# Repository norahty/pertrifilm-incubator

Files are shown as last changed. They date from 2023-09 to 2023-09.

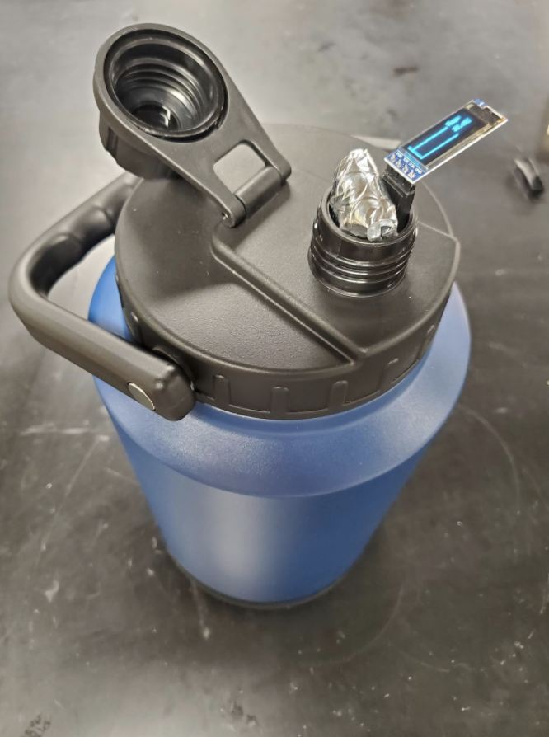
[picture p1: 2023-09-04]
Tests/Ease of Use Test/Final Solution.png

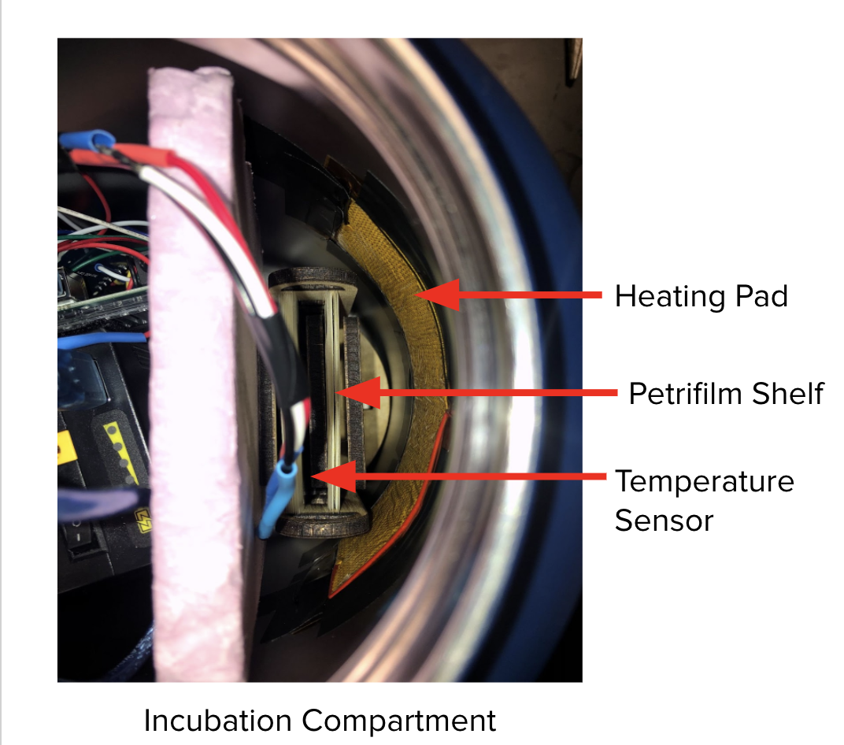
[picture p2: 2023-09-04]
Tests/Ease of Use Test/Incubation Chamber.png

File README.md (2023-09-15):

# Pertrifilm-Incubator Coding Project

This Arduino-based project is coded using C++ to build a portable Petrifilm incubator (a system to inspect e.coli water contamination) for water sample testing in underprivileged areas. It is designed for temperature control in an incubator. It uses various hardware components and libraries to maintain a stable temperature environment for specific applications. This pertrifilm incubator is currently being applied to use by onsite researchers. Below, you will find information on the hardware required, connections, warnings, and the libraries needed for this project.

## Hardware

You will need the following hardware components for this project:

1. 1 x DS18B20 Temperature Sensor
2. 1 x 12V Heater
3. 1 x MOSFET Module (MOS)
4. 1 x Buzzer
5. 1 x Arduino Mega 2560
6. 1 x 0.92 inch OLED Display
7. 1 x SD Card Module
8. Battery (Power Supply)

## Connections

Follow these steps to connect the hardware components to the Arduino Mega 2560:

1. Connect all 5V pins of the components to the Arduino's 5V pin.
2. Connect all GND (Ground) pins of the components to the Arduino's GND.
3. Connect the MOSFET module's IN pin to Arduino's D4.
4. Connect the buzzer to Arduino's D3.
5. Connect the middle pin of the DS18B20 temperature sensor to Arduino's D5.
6. Connect the OLED display's SCL pin to Arduino's SCL.
7. Connect the OLED display's SDA pin to Arduino's SDA.
8. Connect the SD card module's MISO pin to Arduino's 50.
9. Connect the SD card module's MOSI pin to Arduino's 51.
10. Connect the SD card module's SCK pin to Arduino's 52.
11. Connect the SD card module's CS pin to Arduino's 53.

## Warnings

Please take note of the following warnings:

1. Do not set the timer to be lower than or equal to 500ms.
2. Do not touch the heating pad while it is working.
3. Do not let the sensor touch the heater directly.

## Required Libraries

Make sure to install the following libraries in your Arduino IDE before uploading the code:

1. `Adafruit_SSD1306`: Library for OLED display.
2. `DallasTemperature`: Library for DS18B20 temperature sensor.
3. `MsTimer2`: Library for managing timers.

## Arduino Code

You can find the Arduino code for this project in the provided code file. Simply upload this code to your Arduino Mega 2560 to start using the incubator temperature control system.

## Usage

This incubator temperature control system continuously monitors the temperature using the DS18B20 sensor and displays it on the OLED display. It also controls the heater and buzzer based on predefined temperature thresholds. Temperature data is saved to an SD card for later analysis.

Feel free to modify the code and customize the temperature control settings to suit your specific incubation needs.

Enjoy your Arduino-based incubator temperature control project!


Here's a simple demo of how the system works:

temperature control demo:

https://github.com/norahty/pertrifilm-incubator/assets/94091909/2bb5951b-de06-4672-81f7-e4776b39d3b2

the entire incubator:

https://github.com/norahty/pertrifilm-incubator/assets/94091909/0f1d060a-ad9f-48bf-81df-5f7a59860c57

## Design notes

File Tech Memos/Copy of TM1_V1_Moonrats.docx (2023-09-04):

DATE: February 8th, 2021

TO: Dr. Deirdre Hunter

FROM: Sindhuja Darisipudi, Nora Han, Joseph Urso, Michael Tang, Jason Ye

Team Moonrats (5moonrats@gmail.com)

SUBJECT: Water Assessment Incubator Problem Statement and Team Structure

Design Problem Context

Water sanitation is a crisis affecting 780 million people around the world, many of whom live in underprivileged and remote areas. This problem is exacerbated because not all water potability tests (i.e. tests that indicate if water is drinkable) are practical in such settings, as many rely on access to laboratories. One method that does work is via Petrifilms, a culture-based method for detection.

Culture-based methods for the detection of microbial contaminants are the state-of-the-art for water quality analysis in both industrialized and developing countries. Microorganisms exist in many environments and require different temperature conditions for optimal growth. Therefore, creating a temperature-stable incubation environment is a precondition for the reliable detection of microbial contaminants of concern in drinking water. By applying water samples to these Petrifilms and incubating them for 24-48 hours, one can visually inspect for E. coli contamination.

Hence, our task is to build an incubator for the Petrifilms that is suitable for water sanitation tests in these remote areas. Our main design criteria in accomplishing this, as discussed with our client, include small size, ease of use, and data logging capabilities, as elaborated in our problem statement.

Current Design Flaws and Future Solutions:

1. Design solution:

A portable, low-cost incubator for holding petri films will be designed by our team.

Designed for: Public Invention, as a part of an initiative to help monitor water quality in remote settings.

Used by: On the ground experts in remote and low resource settings

2. Limitations of existing solution

In order to monitor water quality in remote & low resource settings, a portable incubator is needed to be transportable, as on the ground workers will often be going from location to location

The existing solution has the limitations of:

i. not providing enough information about the inside temperature to monitor the growing environment of the microorganisms.

ii. not being small enough

3. Potential design solution features

A portable (< 38cm×24.5cm×19cm (dimensions of existing design))*, low-cost (under $500) incubator to hold 20 small petri film (3x4 inches) which has:

i. the ability to provide a constant elevated temperature between 30ºC and 42ºC, as this is the ideal incubation temperature for the petrifilms

ii. a data tracking and digital readout of temperature

iii. rechargeable primary cells that could last the duration of one incubation cycle (up to 48 hours) per one charging

iv. be able to work with minimal repairs for upwards of 3 years

If possible, we would like to have it the following features:

i. A warning mechanism to indicate if the system has failed, the battery is low, or if the temperature has fluctuated out of range.

iii. humidity control inside of the incubator

*client wants it to fit in a backpack.

Team Structures and Activities

Over the course of the Spring 2021 semester (beginning January 25th, 2021 and ending May 14th, 2021), Team Moonrats will produce a prototype, 9 technical memos, and a final design accompanying the final prototype. Table 1 outlines the authors of each technical memo, and the date by which we plan to finish them. Table 2 outlines other major deliverables and an estimate of when we would like to finish them by.

We will produce our deliverables within a $500 budget that has been allocated to our team. In order to meet our goals within the given time frame, we will meet weekly on Tuesdays from 7:00pm - 8:00pm. Below, Table 3 and Table 4 list the contact information of the members and affiliates of Team Moonrats.

Table 1: Tech Memo Author Table

Tech Memo | Finish By | Authors
TM1: Problem Statement | 02/08/2021 | All team members
TM 2: Need-to-Know List and Bibliography | 02/15/2021 | Michael & Joseph
TM 3: Design Criteria | 02/19/2021 | Jason & Nora
TM 4: Brainstorming of design solutions | 02/22/2021 | Sindhuja & Michael
SM 10: Team Pit Stop Reflection | 02/22/2021 | Everyone individually
TM 5: Evaluation of Design Solution | 03/02/2021 | Joseph & Jason
TM 6: Design Plan | 03/08/2021 | Nora & Sindhuja
TM 7: Gantt Chart | 03/22/2021 | Michael & Joseph
SM 11: Identity Reflection | 03/29/2021 | Everyone individually
TM 8: Testing Plan | 04/12/2021 | Jason & Nora
TM 9: Design Solution | 05/05/2021 | All team members
SM 12: Team Post Mortem Reflection | 05/07/2021 | Everyone individually

Table 2: Major Deliverables and Planned Completion Dates

Task | Planned Completion Date
Initial Low Fidelity Prototypes | 1st Week of March
Final Low Fidelity Prototype | 2nd Week of March
Select Design & Order Materials | 3rd Week of March
Final Design & Prototype | Late April

Table 3: Team Members and Contact Information

Team Moonrats
Name | Email | Phone Number
Joseph Urso | jru1@rice.edu | +1 (832) 496-4116
Jason Ye | jy76@rice.edu | +1 (832) 245-6714
Sindhuja Darisipudi | sd87@rice.edu | +1 (972) 662-8299
Michael Tang | mjt6@rice.edu | +1 (713) 349-3952
Nora Han | th42@rice.edu | +86 131 4118 1917

Table 4: Clients, Sponsors, and Other Affiliates and Contact Information

Name | Role | Email
Dr. Christopher Ferguson | Client | cfergu11@gmail.com
Dr. Ashley Taylor | Faculty Sponsor | art6@rice.edu
Scott Lin | Design Mentor | sl105@rice.edu
Cat Grasso | Writing Mentor | cg39@rice.edu

Works Cited

“Global WASH Fast Facts.” Global Water, Sanitation, & Hygiene (WASH), Center for Disease Control and Prevention, 11 April 2016, https://www.cdc.gov/healthywater/global/wash_statistics.html. Accessed 5 February 2021.

Mistry, Pratibha, and Jessica A. Lawson. “Testing water quality: When labs don’t work.” World Bank Blogs, World Bank Group, 24 January 2017, https://blogs.worldbank.org/water/when-labs-don-t-work. Accessed 7 February 2021.

Schertenleib, A., Sigrist, J., Friedrich, M. N. D., Ebi, C., Hammes, F., Marks, S. J. Construction of a Low-cost Mobile Incubator for Field and Laboratory Use. J. Vis. Exp. (145), e58443, doi:10.3791/58443 (2019). Accessed 7 February 2021.

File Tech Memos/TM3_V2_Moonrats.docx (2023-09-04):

DATE: March 2nd, 2021

TO: Dr. Deirdre Hunter

FROM: Sindhuja Darisipudi, Nora Han, Joseph Urso, Michael Tang, Jason Ye[^1]

Team Moonrats (5moonrats@gmail.com)

SUBJECT: Water Assessment Incubator Design Criteria

Introduction

1. Relevant Context for the Engineering Design Process

Our client needs a 3M™ E. coli detection Petrifilm[^2] incubator to provide a stable temperature environment for 24-48 hours. Currently, he has identified several problems with their existing incubator (“The Armadillo Incubator”) and has asked us to create an improved, low-cost and portable incubator for these Petrifilms that is suitable for water sanitation testing research in remote areas that lack lab resources.

According to our previous meeting with our client, we identified several potential design solution features of a portable, low-cost incubator to hold 20 small petri film (3x4 inches) which has: the ability to provide a constant elevated temperature; a data tracking and digital readout of temperature; rechargeable primary cells that could last the duration of one incubation cycle per one charging; be able to work with minimal repairs. If possible, we would like to have the following features: a warning mechanism to indicate if the system has failed, the battery is low, or if the temperature has fluctuated out of range; a humidity control inside of the incubator

2. Overview of Decision Process & Reasons of Research decisions

Our team generated a list of design criteria and constraints during class discussion (Feb, 9, 2021) and our weekly team meeting (Feb, 9, 2021). The constraints of our design criteria are mainly based on client requests and quantitative research. In some cases, the client has provided us with quantitative requirements, whose parameters agree with our additional research. The objectives are mainly based on client requests and will be evaluated by the users. Detailed explanations of each criteria are included in the conclusion section. We started by listing out the criteria without the numbers (low cost, small size, easy to make, easy to use, be in temperature range, battery life, durability, battery alarm, temperature alarm, data tracking system). Then, on the basis of our interview with our client (Feb, 5, 2021), we identified which criterias are constraints (be in temperature range, and safety) based on our need-to-know list and research in TM_2. Finally, we confirmed a reasonable list of design criteria (low cost, size, easy to make, easy to use, durability, battery duration and adjustable temperature).

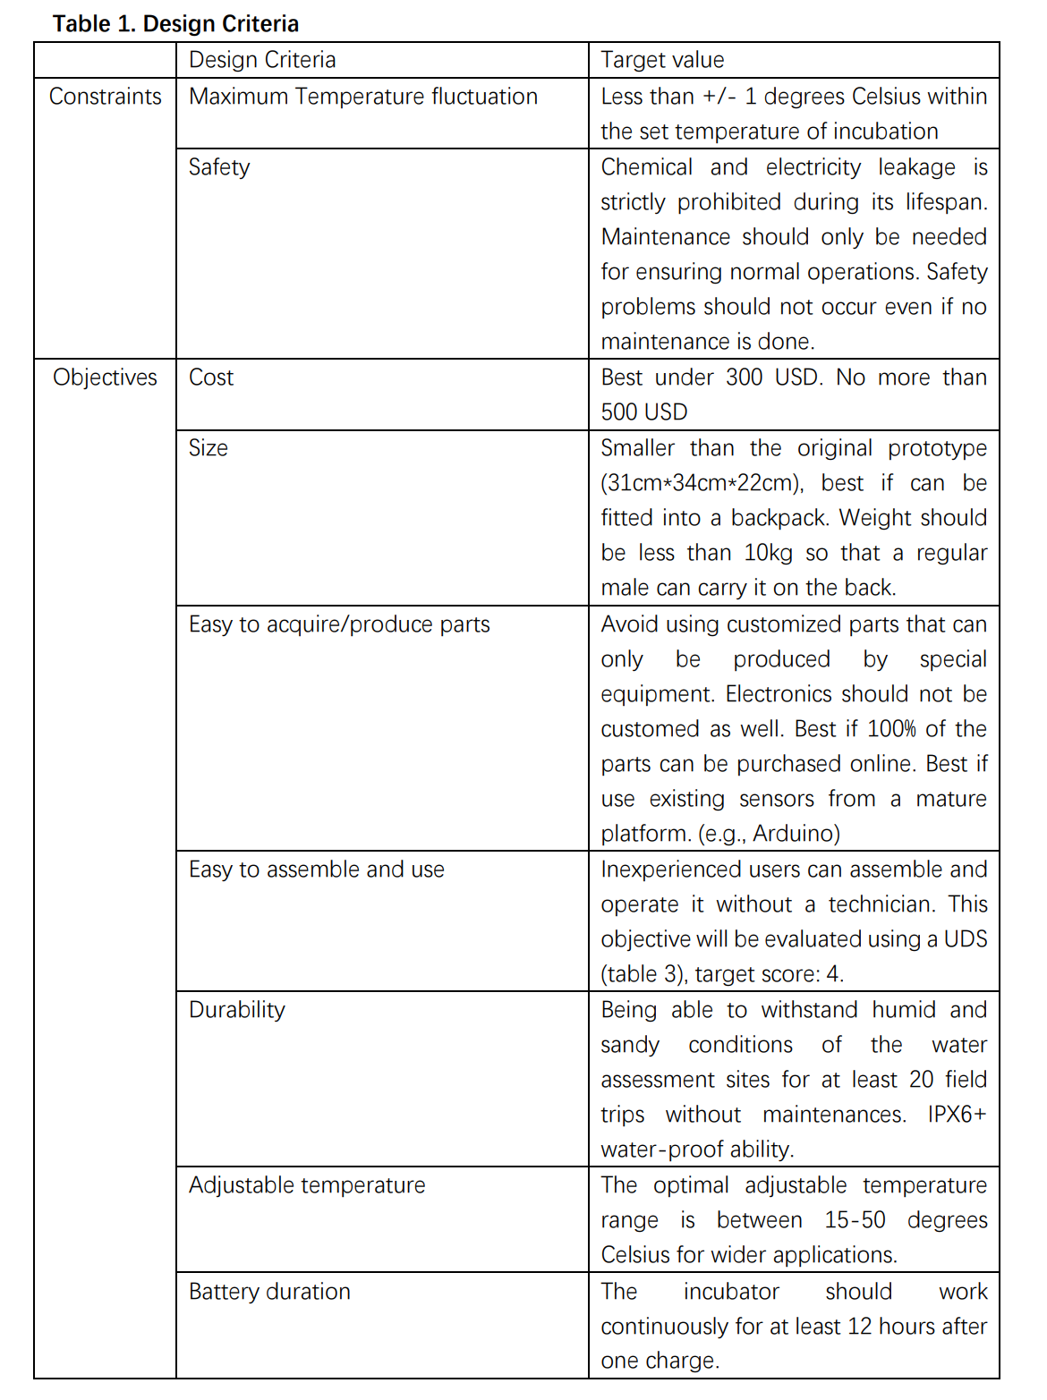
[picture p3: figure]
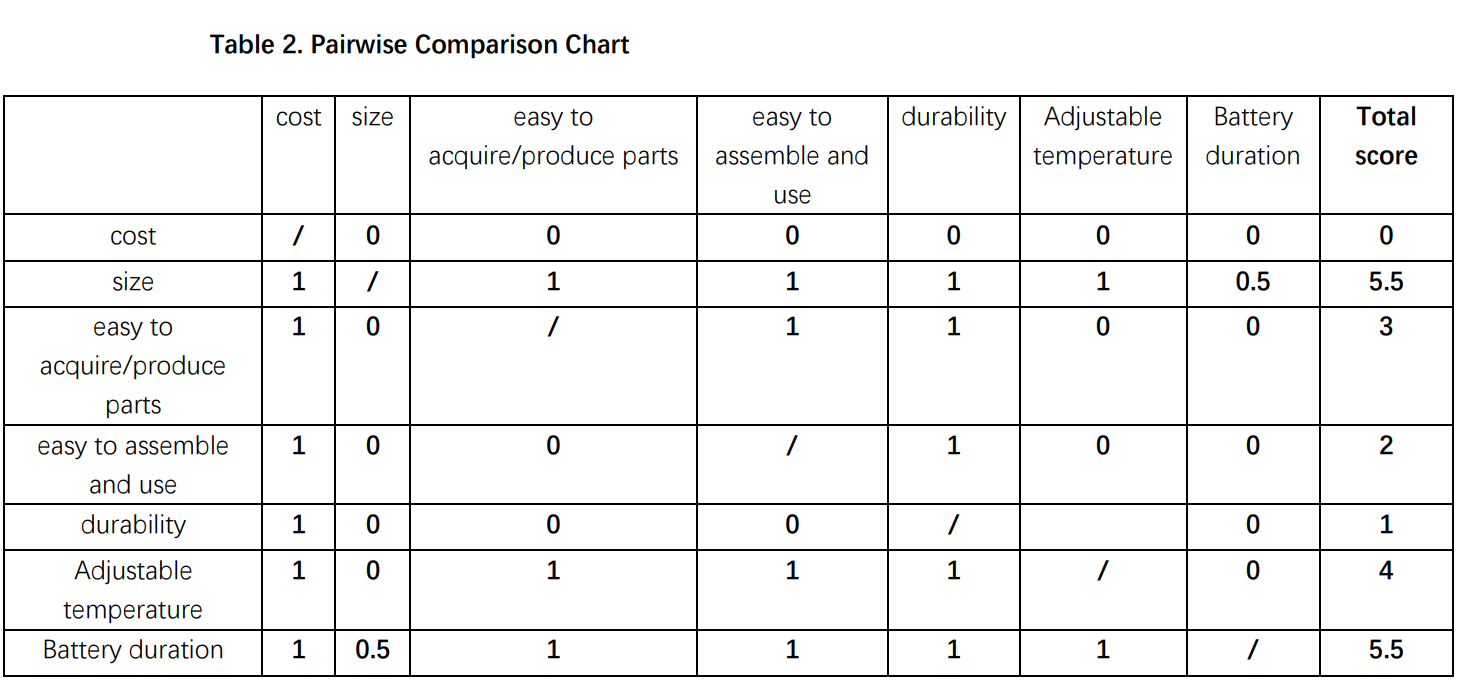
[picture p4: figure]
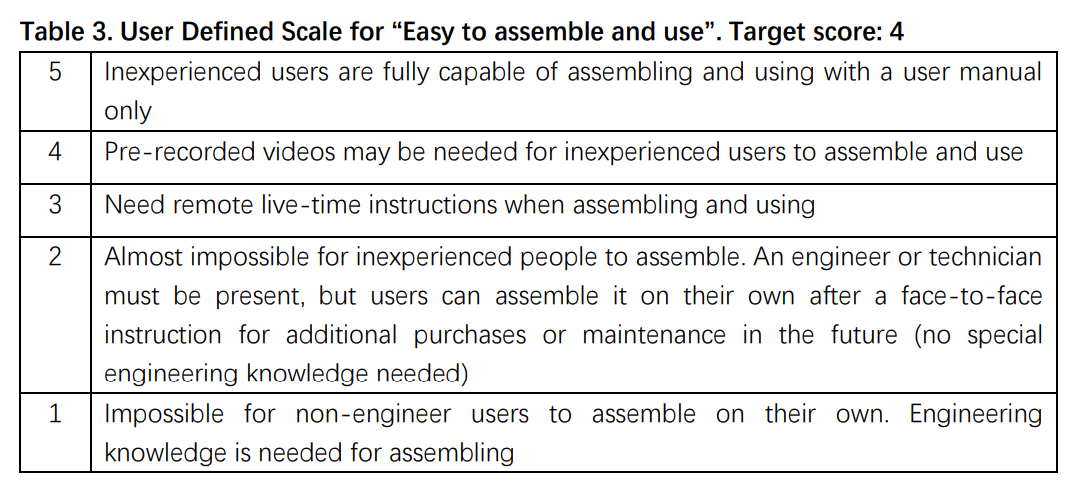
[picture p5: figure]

Conclusion

Detailed explanations of each design criteria in table 1 are shown below:

Constraints:

1) Maximum allowed temperature fluctuation: +/- 1 degree Celsius

We have set the maximum allowed temperature fluctuation to be +/- 1 degree Celsius based on the existing biological incubator models and the user manual of a typical 3MTM Petrifilm. Some existing models have a fluctuation of +/- 2 degrees Celsius, but the recommended temperature fluctuation of 3MTM Petrifilm from its user manual is +/- 1 degree Celsius. Since the client stated that the standard 3MTM Petrifilm will be used mostly in water assessment, we have set this constraint to meet the client requirement.

2) Safety: 0 safety problem allowed during its lifespan

Since the battery will likely be a massive one, a leakage of either its chemical contents or electricity can cause serious accidents. Also, if we use chemical reactions as a heating method, these chemicals can be harmful to the human body as well. Therefore, in order to ensure the safety of its users, we have set the constraint to be no leakage of any kind is allowed even if the incubator does not receive regular maintenance.

The objectives are mainly based on client requests. Based on the nature of some objectives, it is hard to quantify some of them. For these objectives, we will use a user defined scale to evaluate our design.

Objectives:

The relative importance of each objective is compared and calculated in table 2, pairwise comparison chart.

1) Cost: cannot exceed 500 USD

The cost should be under 300 USD if possible. However, based on additional features and smaller size, the client is willing to pay a maximum of 500 USD for one model.

2) Size: must be smaller than the original prototype

The size of the original prototype is 31cm*34cm*22cm. The minimum requirement is that our model cannot be bigger than the original prototype. It is preferred that the incubator can fit into a typical backpack. Therefore, our eventual goal is to make the incubator smaller than 30cm*25cm*15cm, approximately.

3) Easy to acquire/produce parts

Since water assessment is conducted mainly in suburban areas of developing or under-developed countries, sometimes it is hard to acquire customized parts, and biologists may not be familiar with mechanical components of the incubator. Therefore, we should use existing parts as much as possible, and try to avoid using parts that can only be manufactured by special equipment. The best case scenario is that 100% of the parts can be purchased online through some widely used shopping websites, such as Amazon, and no special tools other than basic electric tools (drills, electric saws) are needed.

4) Easy to assemble and use

Biologists are not engineers. They may not fully understand how the incubator works. Since they are the users, we should consider the user-friendliness of our product. They should be able to assemble and operate the incubator with only a user manual and potentially pre-recorded tutorial video and without the help of an engineer or technician on site. If we achieve this ultimate goal, we will receive a score of 4 on our UDS.

5) Durability

This incubator is not lab equipment. It needs to withstand the possibly severe environmental and weather conditions of the testing site and during transportation. We expect it to be at least better than IPX6, which means no water can pass through its outer shell under high-pressure, heavy-sprays of water.

6) Adjustable temperature: 15-50 degrees Celsius

The client requires the temperature of the incubation chamber to be adjustable in order to meet the incubation requirements of different germs, possibly further applications other than water assessment. From the data provided by Biodiversity of Fungi and Separation Science and Technology, the adjustable range between 15 and 50 degrees Celsius allows the incubation of most common germs.

7) Battery duration: >=12 hours

We have set the minimum battery duration after a single charge to be >= 12 hours. This is a client requirement. Additionally, according to the Journal of Clinical Microbiology, the Association for the Advancement of Medical Instrumentation recommends all cultures should be incubated for at least 12 hours(one cycle of incubation) on suitable culture media before further observation. Therefore, in order to guarantee the accuracy of further observation after incubation, and according to our client’s requirement, we decide to follow the above guidance.

The driving force of our design criteria is mostly a combination of client request and our research. The client has set many goals for us, in which we listed all of them in our design objectives. Since most of his requests are as brief as basic descriptions of the functions that are preferred to have, we also did our research to further quantify the target functions.

As for the most difficult part of constraints, we think that the battery duration will be our biggest challenge. We cannot make the battery smaller because of the limitations of modern-day battery technologies. The minimum duration of 48 hours will require a huge battery, which occupies a lot of precious space. Due to the huge size and limited capacity of battery, we will need to consider the layout of other components very carefully to minimize the size of our incubator. Also, we need to consider the method of heating and cooling if needed to maximize the energy efficiency.

The most difficult part of objectives is to minimize the size while making it easy to manufacture at the same time. We think that a very important and useful way of reducing the size is to use customized parts so that no space is wasted. We will discuss how to address this issue later.

Our team is working very efficiently. Everyone is highly motivated and is comfortable with expressing his/her insights during Zoom meetings both in and out of class time. The key to our productions of every tech memo is creating an equal and comfortable atmosphere of discussion and valuing everyone’s opinions. Our team is also driven by everyone’s passion and dedication into this project. The most memorable moment is that even during this hard time of blackout, everyone tried their best to contribute to this tech memo by attending meetings and researching useful materials.

Citation:

1. https://www.3m.com/3M/en_US/company-us/all-3m-products/~/ECOLICT-3M-Petrifilm-E-coli-Coliform-Count-Plates/?N=5002385+3293785155&rt=rud
2. https://www.ncbi.nlm.nih.gov/pmc/articles/PMC270135/
3. https://www.sciencedirect.com/topics/immunology-and-microbiology/incubation-temperature
4. https://www.3m.com/3M/en_US/company-us/all-3m-products/~/ECOLICT-3M-Petrifilm-E-coli-Coliform-Count-Plates/?N=5002385+3293785155&rt=rud

[^1] Main Writers: Nora Han and Jason Ye
[^2] See details at: https://www.3m.com/3M/en_US/company-us/all-3m-products/~/ECOLICT-3M-Petrifilm-E-coli-Coliform-Count-Plates/?N=5002385+3293785155&rt=rud

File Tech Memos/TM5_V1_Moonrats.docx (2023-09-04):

DATE: March 8, 2021

TO: Dr. Deirdre Hunter

FROM: Sindhuja Darisipudi, Nora Han, Joseph Urso, Michael Tang, Jason Ye[^1]

Team Moonrats (5moonrats@gmail.com)

SUBJECT: Screening, Scoring and Selection of Water Assessment Incubator Solution

Screening, Scoring and Selection Overview

Our team is designing a portable incubator to provide a stable temperature environment for 3M™ E. coli detection Petrifilms[^2]. We evaluated our brainstormed solutions and have combined them into several complete solutions.. Figure 1 represents a flowchart of our selection process.

Our design includes many intricate parts, so we brainstormed ideas for each design block. Our design blocks included data logging, digital display, heating, insulation, power source, and the shape of the design. Because we split up the design in this manner, we formed many partial/component solutions. After brainstorming solutions, we combined the ideas into a Morph Chart (Figure 2). Upon further examination, we identified that our Morph Chart had too many options. At this point, we decided to screen our design block solutions against the design criteria. Our goal was to have ≤ 5 options for each design block. Therefore, we decided to screen all design blocks with > 5 solution options. We created a screening matrix for heating, insulation, and shape/form. These screening matrices can be seen respectively in Figure 3, Figure 4, and Figure 5. After narrowing our options for each design block, we created a final Morph Chart (Figure 6). Using the final morph chart, each member of our group created 2-3 complete solutions.

After creating complete solutions, we took turns and explained our solutions to one another. We wanted each member to fully understand each solution that was to be scored. Once we were all on the same page, we proceeded to score them against each other (Figure 7). In total, we scored 11 solutions. We created a proxy for battery duration, ease of fabrication, and durability. All details regarding proxies and scales used for scoring can be found in Figure 8 and in the section “Proxies for Scoring”.

After scoring, we selected our top 4 scoring solutions and identified popular components amongst the high scoring solutions. By identifying popular components, we wanted to identify which items seemed “most reliable” or “important to the design”, and attempted to include these within our final design. Ultimately, we chose to move forward with solution I. We believe solution I was the most feasible of all our top solutions. Solution I requires one fabricated part and the remainder of parts can be ordered online. Additionally, its cost is average and a thermos would be smaller than the existing solution. Finally, the insulation method is extremely efficient (vacuum insulation) and this would result in lower power consumption in order to maintain temperature within our design. The battery and control system will be located at the bottom of the device. There will be a separate mechanism for holding the Petrifilms. We will wrap heating tape around the inside layer of our Thermos. Figure 9 is a preview of our selected design.

Proxies for Scoring

Our proxy for battery duration is based on an imaginary parameter called “electricity score”. This score is based on the number of components that will require power. Additionally, we take into account the effects of insulation. A better insulator will require that we use less power, so a better insulator will subtract 1 from the electricity score. A worse insulator will add 1 to the electricity score. The distinction between “better” or “worse” insulators was decided in our insulation screening matrix. More information on “best insulator” can be found in Figure 4.

Our proxy for ease of fabrication is based on the number of fabricated parts. Below is a list of what is considered a fabricated part:

- Having to fasten/attach battery to a surface
  - Rather than placing it inside
- Having to fasten/attach heating element to a surface
  - Ex: Taping/gluing/screwing in heating pad to a surface
- Modifying foam, reflective insulation bags, or wood wool to fit into device
- Modifying outer shell for place to put the digital display
- Implementing a emergency battery pack to function after main power source is low
- Implementing a light indicator
- Structured foldable structure or rollable insulation bag
- Creating/implementing supports for foldable structure or insulation bag
- Creating casing/mechanism for holding perti-films or moving them in and out of device

Our proxy for durability is dependent on the number of “weak” components. A weak component is a component that is easily damaged or will have to be replaced regularly (approximately 3-6 months). We add 1 to the score for each weak component. The list of weak components include:

- OLED/LED or LCD Screen
- Heating Pad
- Soft outer case

Results of Screening, Scoring, and Selection

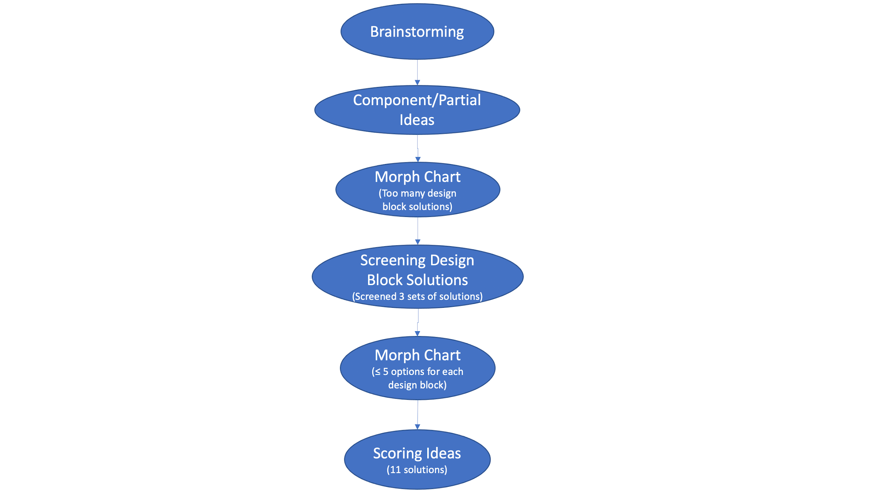
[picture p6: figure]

Figure 1: Flow Chart for Our Selection Process (missing)

Design Blocks | Option 1 | Option 2 | Option 3 | Option 4 | Option 5 | Option 6 | Option 7 | Option 8
Data Logging | Light indicator | Bluetooth to smartphone | Built in Smartphone | Digital thermometer | Serial Port
Digital Display | OLED Screen | LCD Screen | Live Data Display | Battery % represented | None
Heating | Heating Pad | Heating by liquid | Heating coil | Heat tape | Capturing energy from outside environment | use lens to focus sunlight
Insulation | Packing styrofoam | Reflective insulation bags | Vacuum Sealing Insulator | Packing Peanuts | Yeti Cup Casing | Bubblewrap | Nomex | Wood wool
Power Source | Rechargeable (car adapter) | Rechargeable battery (AC adapter) | Disposable battery pack (AA or D) | Easily removable battery pack | Emergency battery pack
Shape/Form | Rollable insulation bag (tri-prism) | Structured foldable structure | Cylindrical (Thermos or Yeti Cup) | rectangular prism | Sphere | Collapsible structure

Figure 2: Initial Morph Chart

Note: We did not use this Morph Chart to generate solutions. Upon examination, we thought this Morph Chart had too many solutions for certain design blocks.

| Heating Pad | Heating by liquid | Heating coil | Heat tape | Capturing energy from outside environment | Use lens to focus sunlight | Lightbulb
Cost | 0 | -1 | -1 | 0 | -1 | 1 | 1
Size | 0 | -1 | 0 | 1 | 0 | 0 | -1
Ease of Fabrication | 0 | -1 | 0 | -1 | -1 | -1 | -1
Durability | 0 | -1 | 1 | 1 | 0 | -1 | -1
Battery Duration | 0 | -1 | 0 | 0 | 1 | 1 | -1
TOTAL | 0 | -5 | 0 | 1 | -1 | 0 | -3

Figure 3: Screening Matrix for Heating Methods

Note: Solutions that made it to the final Morph Chart are highlighted in grey.

| Packing styrofoam | Reflective Insulation Bags | Packing Peanuts | Yeti Cup Casing | Bubblewrap | Nomex | Wood wool | Foam | Cooler | Fiberglass
Cost | 0 | 0 | 0 | -1 | 0 | -1 | 0 | 0 | -1 | -1
Size | -1 | 1 | -1 | 1 | 0 | 1 | -1 | 0 | 0 | 0
Ease of Fabrication | 0 | 0 | 0 | 1 | 0 | 0 | 0 | 0 | 1 | 0
Durability | -1 | 1 | -1 | 1 | -1 | 0 | -1 | 0 | 1 | 1
Battery Duration | 0 | -1 | 0 | 1 | -1 | -1 | -1 | 0 | 1 | -1
TOTAL | -2 | 1 | -2 | 3 | -2 | -1 | -3 | 0 | 2 | -1

Figure 4: Screening Matrix for Insulation Methods

When comparing each solution against battery duration, we considered the quality of each insulator. The quality of the insulator is dependent on its thermal conductivity.

| Rollable Insulation Bag (Tri-Prism) | Structured Foldable Structure | Cylindrical (Thermos or Yeti Cup) | Rectangular Prism (Cooler) | Sphere | Collapsible Structure
Cost | 1 | 1 | 0 | 0 | -1 | 0
Size | 1 | 1 | 1 | 0 | 1 | 1
Ease of Fabrication | -1 | 1 | 1 | 0 | -1 | -1
Durability | -1 | -1 | 0 | 0 | -1 | -1
Battery Duration | 0 | 0 | 0 | 0 | 0 | 0
TOTAL | 0 | 2 | 2 | 0 | -2 | -1

Figure 5: Screening Matrix for Shape of our Design

For this set of solutions, battery duration is unrelated to the shape of the design. Therefore, a 0 was put in place for all solutions.

Design Blocks | Option 1 | Option 2 | Option 3 | Option 4 | Option 5
Data Logging | Light indicator | Bluetooth to smartphone | Built in smartphone | Digital thermometer | Serial Port
Digital Display | OLED Screen | LCD Screen | Live data display | Battery % represented | None
Heating | Heating Pad | Heating coil | Heat tape
Insulation | Cooler | Reflective insulation bags | Foam | Fiberglass | Yeti Cup Casing
Battery | Rechargeable (car adapter) | Rechargeable battery (AC adapter) | Disposable battery pack (AA or D) | easily removable battery pack | Emergency battery pack
Shape | Rollable insulation bag (tri-prism) | Structured foldable structure | Cylindrical (Thermos or Yeti Cup) | rectangular prism

Figure 6: Final Morph Chart

Design Criteria | Weight | Solution A | | Solution B | | Solution C | | Solution D | | Solution E
| | Rating | Weight Score | Rating | Weight Score | Rating | Weight Score | Rating | Weight Score | Rating | Weight Score
Size | 30% | 1 | 0.3 | 2 | 0.6 | 1 | 0.3 | 2 | 0.6 | 1 | 0.3
Battery Duration | 30% | 5 | 1.5 | 3 | 0.9 | 4 | 1.2 | 3 | 0.9 | 4 | 1.2
Ease of Fabrication | 20% | 3 | 0.6 | 4 | 0.8 | 3 | 0.6 | 2 | 0.4 | 4 | 0.8
Durability | 10% | 4 | 0.4 | 4 | 0.4 | 4 | 0.4 | 4 | 0.4 | 4 | 0.4
Cost | 10% | 4 | 0.4 | 3 | 0.3 | 3 | 0.3 | 2 | 0.2 | 1 | 0.1
TOTAL | | | 3.2 | | 3 | | 2.8 | | 2.5 | | 2.8

Design Criteria | Weight | Solution F | | Solution G | | Solution H | | Solution I | | Solution J | | Solution K
| | Rating | Weight Score | Rating | Weight Score | Rating | Weight Score | Rating | Weight Score | Rating | Weight Score | Rating | Weight Score
Size | 30% | 4 | 1.2 | 4 | 1.2 | 3 | 0.9 | 2 | 0.6 | 1 | 0.3 | 5 | 1.5
Battery Duration | 30% | 2 | 0.6 | 2 | 0.6 | 4 | 1.2 | 5 | 1.5 | 5 | 1.5 | 2 | 0.6
Ease of Fabrication | 20% | 1 | 0.2 | 1 | 0.2 | 2 | 0.4 | 5 | 1 | 4 | 0.8 | 3 | 0.6
Durability | 10% | 2 | 0.2 | 2 | 0.2 | 4 | 0.4 | 5 | 0.5 | 3 | 0.3 | 2 | 0.2
Cost | 10% | 3 | 0.3 | 2 | 0.2 | 1 | 0.1 | 3 | 0.3 | 5 | 0.5 | 5 | 0.5
TOTAL | | | 2.5 | | 2.4 | | 3 | | 3.9 | | 3.4 | | 3.4

Figure 7: Scoring Matrix

Solutions highlighted in gray were our four highest scoring solutions.

Design Criteria | Proxy | Scoring Matrix Ranking
Battery Duration | Electricity Score (ES = Electricity Score) (see explanation above) | 5: ES = 1
| | 4: ES = 2
| | 3: ES = 3
| | 2: ES = 4
| | 1: ES ≥ 5
Ease of Fabrication | # of fabricated parts (see above for what is considered a “fabricated part”) | 5: 1 part
| | 4: 2 parts
| | 3: 3 parts
| | 2: 4 parts
| | 1: ≥ 5 parts
Durability | Based on # of weak components (see above for “weak components”) | 5: 0 weak components
| | 4: 1 weak component
| | 3: 2 weak components
| | 2: 3 weak components
| | 1: ≥ 4 weak components
Cost | N/A | 5: ≤ $100
| | 4: $100 - $115
| | 3: $115 - $130
| | 2: $130 - $145
| | 1: ≥ $145
Size | N/A | 5: ≤ 200 cubic inches
| | 4: 400 - 200 cubic inches
| | 3: 600 - 400 cubic inches
| | 2: 2000 - 600 cubic inches
| | 1: ≥ 2000 cubic inches

Figure 8: List of Scales and Proxies Used in Scoring

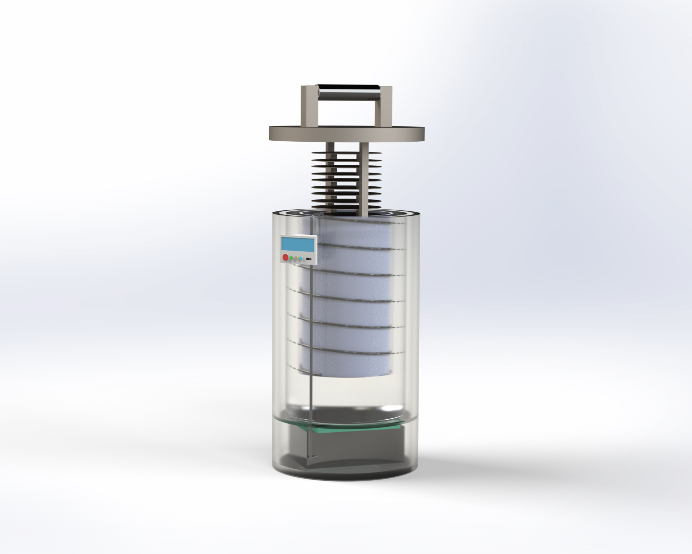
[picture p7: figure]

Figure 9: Preview of our Selected Solution

Conclusion

1. What were key features that helped distinguished between solutions?

We believe that the most important feature of the selected solution is the form factor, which is the combination of insulation and shape as we choose to use a thermos. Although thermos don’t score high in size, its vacuum insulation is very effective in saving energy. Moreover, although our major mission in this project is to reduce the size of the incubator, the solutions that score the highest in size (foldable structures and rollable structures) have rather poor insulation and potential durability problems. We think that for the above two transformable structures, everything has to be thin enough so that the users can transform them easily and without damaging crucial parts, such as the insulating material. Folding or rolling a thick piece of foam may cause damage to the foam, and as a result will affect insulation effectiveness, which can cause higher energy emission that leads to a higher energy consumption from the battery.

Another concern with foldable and rollable structures is that comparing to rigid form factors, these two structures provide weaker support and protection for other parts, especially battery and control board, under severe working conditions. The incubator needs to work in the testing site, which typically is in the wild by the river, so it is important for it to be water-proof, but it’s much harder to seal transformable structures tight than rigid structures. Also, the incubator will most likely to be transported in the back of a truck, so the whole body needs to be strong enough to protect important parts from bumpings and collisions. We think that rigid shells do much better than soft shells in that.

In conclusion, for the form factor part, considering both insulation ability and strength of the structure, we think that a thermos is the best choice.

2. What features of your process heavily influenced solution selection?

The quantified 1-5 values heavily influenced our solution selection. Take battery duration in our scoring matrix as an example. We conclude that battery duration is mainly decided by three factors: the number of electric components it has to power, the effectiveness of insulation (because better insulation prevents energy emission, which saves power), and whether there will possibly be space for extra battery. We define the raw score of battery duration by adding the number of electric components it needs to power, plus one if the insulation method of that solution is poor, minus one if the insulation is good, and finally minus one if there is extra space for back-up battery.

When deciding if the insulation is good or not in this section, we first analyze the Fourier’s Law for heat conduction, which states that the speed of heat transfer is directly proportional to the thermal conductivity of the material. Therefore, we should consider two factors: the thermal conductivity (the lower the better for insulation) of the insulating material and how thick the material can be in the solution. For example, for Yeti cup casing and thermos, the insulation is basically a vacuum, which theoretically has a thermal conductivity of 0, so it is definitely a good insulation method regardless of the thickness. For other materials such as Styrofoam, which has a thermal conductivity of 0.033, thickness has to be taken into consideration. In a rigid container such as a cooler, we can place very thick foam around the incubation chamber, so it’s also a good insulation. However, for rollable structures and foldable structures, we may not be able to fold or roll very thick foam, so they are considered poor insulation.

After calculating the raw scores, which range from 1-5, we transfer them into scores in the scoring matrix. A raw score of 1 corresponds to a 5 in the scoring matrix, and a raw score of 5 corresponds to a 1 in the scoring matrix.

For other design criteria in the scoring matrix, we use a similar approach. For durability, we estimate the number of design parts in the solution that are most likely to cause a reliability problem in severe working conditions. For ease of fabrication, we estimate the number of customized parts in each solution that may require special manufacturing processes or can only be ordered from manufacturers.

3. What salient process decisions were made during solution selection?

One of the salient decisions we made during scoring is that we decided to remove cooling system and the design criterion of adjustable temperature in screening and scoring after we meet with Dr. Read and reconsider the process of incubation. We initially wanted to include a cooling system because we imagined that the incubator would function as an air-conditioner for Petrifilms that could both increase and decrease the temperature during incubation. However, we realized that there can’t be a scenario which requires the incubator to decrease the temperature after the incubation starts. Therefore, we redefined “adjustable temperature” as to be able to set different incubation temperatures before the incubation. To this end, we believe that this function can be realized fully by programming, so it’s not necessary to include this in the scoring matrix which mainly decides the hardware of the incubator.

4. What were the memorable moments or discussions that led to breakthroughs in process and/or products?

One of the memorable moments is that the whole group and Scott had a 5-hour meeting from 8pm to 1am in the morning. Before this meeting, we were a bit behind schedule, but fortunately, we were able to sort so many things out during that meeting. Everyone participated in the discussion and was researching for supporting materials for screening and scoring. After this meeting, we felt so relieved because one of the most difficult parts of ENGI 120 has passed and we made it. Everything was back on track after that night. We were tired, but our group work finally produced dream work.

[^1] Main Writers: Joseph Urso and Jason Ye
[^2] See details at: https://www.3m.com/3M/en_US/company-us/all-3m-products/~/ECOLICT-3M-Petrifilm-E-coli-Coliform-Count-Plates/?N=5002385+3293785155&rt=rud

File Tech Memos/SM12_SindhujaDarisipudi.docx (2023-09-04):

DATE: May 8th, 2021

TO: Dr. Deirdre Hunter

FROM: Sindhuja Darisipudi

SUBJECT: Portable, Data Logging Incubator Post-Mortem

Introduction

Our client is utilizing 3M Petrifilms for E.coli detection, a culture-based method for the detection of microbial contaminants. However, these films require a temperature-stable incubation environment in order to reliably detect microbial contaminants of concern in drinking water. Currently, they have identified several problems with their existing incubator (“The Armadillo Incubator”) and have asked us to create an improved, low-cost and portable incubator for these Petrifilms that is suitable for water sanitation testing research in remote areas that lack lab resources. Our design challenge is to build an incubator for the Petrifilms that is suitable for water sanitation tests in these remote areas.

Post-Mortem

Planning, especially through a Gantt chart, has allowed us to break down our complex problem and moving parts into a easy to tackle, digestible portions. It has also allowed us to delegate parts of our design to various team members, and hold ourselves accountable to meeting deadlines. The division of labor allowed us to make this project a manageable task, and allowed us to keep making progress even when certain members had high workloads or other tasks in their personal lives. In order to keep cohesion with all of the various components and aspects of our project, our team met at least once a week outside of class, in combination with prototyping sessions. We also frequently texted each other in our group chats in order to keep each other updated on progress. Last, we had meeting notes for each meeting to keep those who missed meeting on track with what we were working on.

In order to make design decisions, we spoke to each team member, and we each voiced our opinions. After we talked through our opinions, we talked through the strengths and weaknesses of each potential solution and came to a consensus as a group.

Our final prototype was extremely successful, as we met almost all of our design criteria. We believe that we will be able to meet the final design criteria that we have not tested yet. Our prototype was able to successfully perform an incubation cycle.

Our entire team worked very well together, but we still have areas to grow in our communication. This is likely due to the fact that we all had different priorities and desires for our project. Communicating our goals better together in the beginning would have assisted us in tackling this project.

In the future, having a common set of goals and a structured plan from before the point at which we created a Gantt chart would have helped us be a more effective team. Other than that, our work in creating deliverables and a working prototype was extremely successful, and continuing to work in that manner would help us continue to be a good group

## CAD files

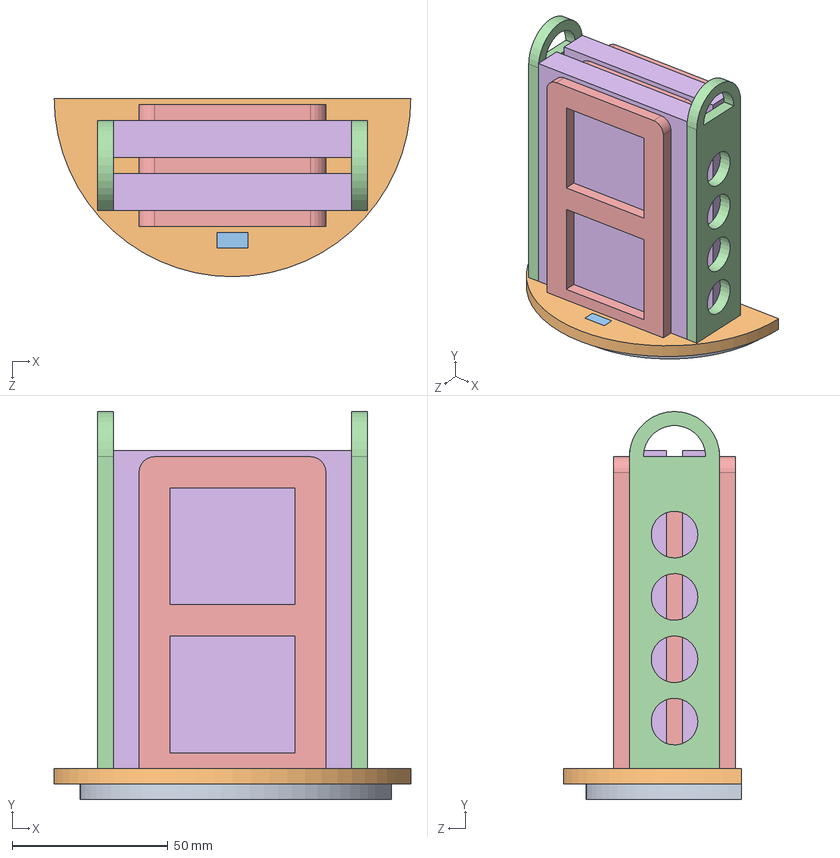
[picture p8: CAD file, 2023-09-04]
CAD models/Assem1.SLDASM
114.4 x 124.5 x 57.2 mm
base
upper base
connector
beam1 x 2
beam2 x 3
10_petrifilms x 2

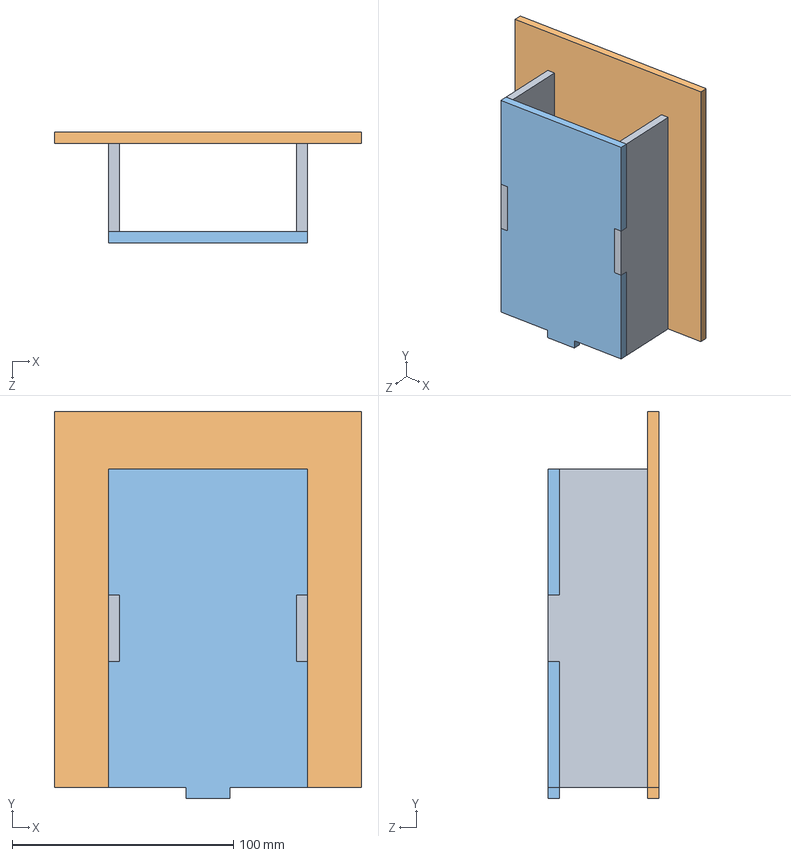
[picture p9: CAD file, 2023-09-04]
CAD models/battery box.SLDASM
139.0 x 175.0 x 50.0 mm
battery_side x 2
Battery_front
Battery_rear

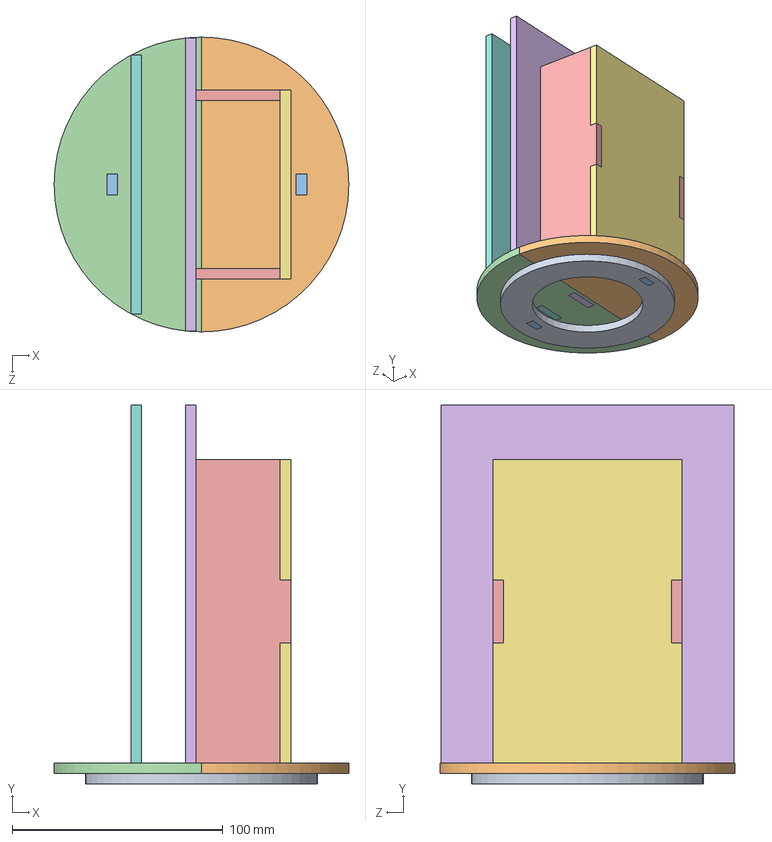
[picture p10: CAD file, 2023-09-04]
CAD models/final.SLDASM
140.0 x 180.0 x 140.0 mm
base_final
upper base_final
alignment x 2
upper baseup_final
battery_side x 2
Battery_front
Battery_rear
foam case

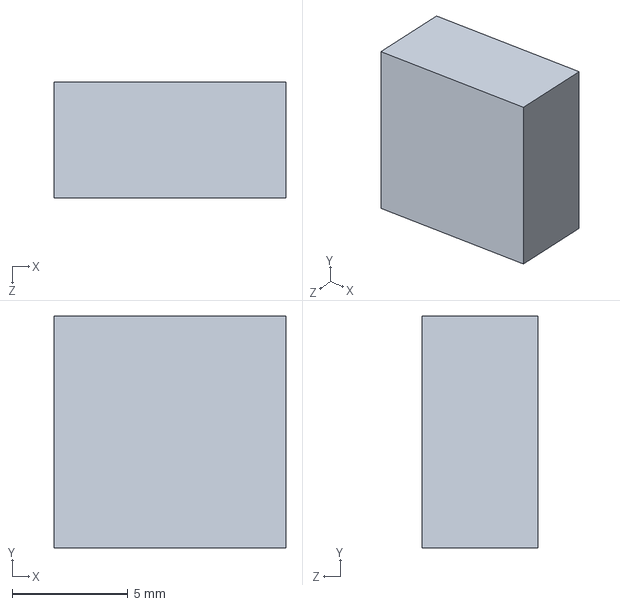
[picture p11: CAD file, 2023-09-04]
CAD models/connector.SLDPRT
10.0 x 10.0 x 5.00 mm

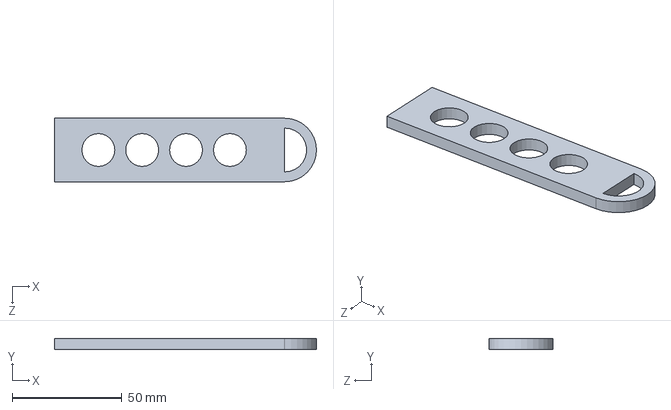
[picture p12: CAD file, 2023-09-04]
CAD models/beam1.SLDPRT
119.5 x 5.00 x 29.0 mm

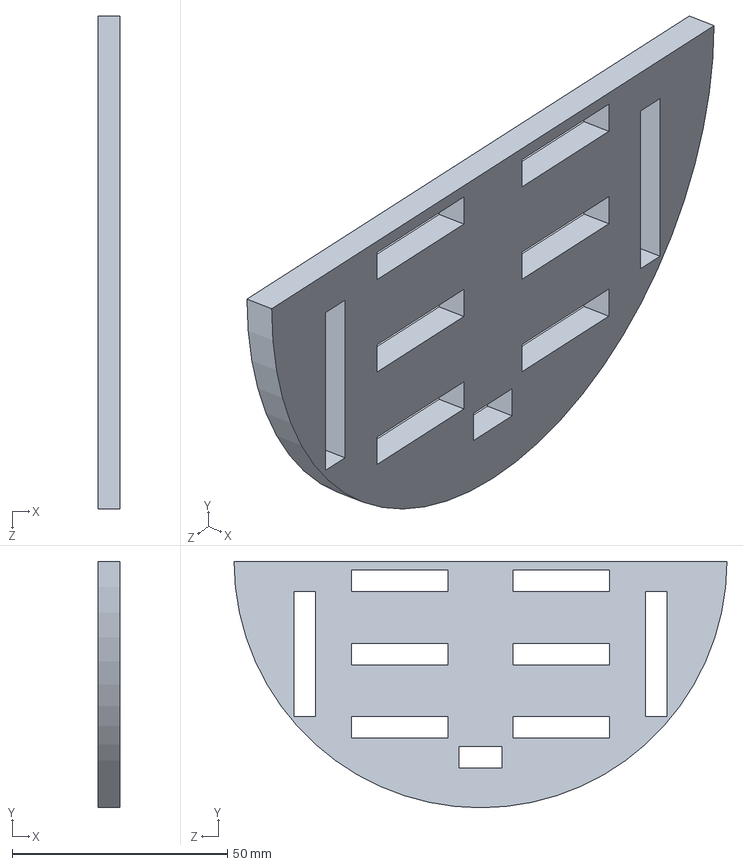
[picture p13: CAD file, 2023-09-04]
CAD models/upper base.SLDPRT
5.00 x 57.2 x 114.4 mm

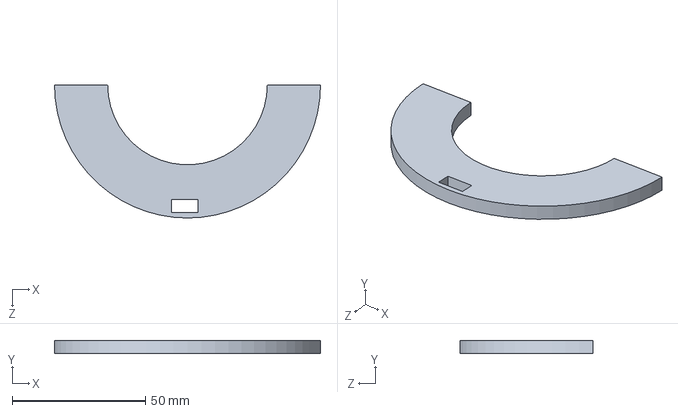
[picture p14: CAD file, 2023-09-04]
CAD models/base.SLDPRT
100.0 x 5.00 x 50.0 mm

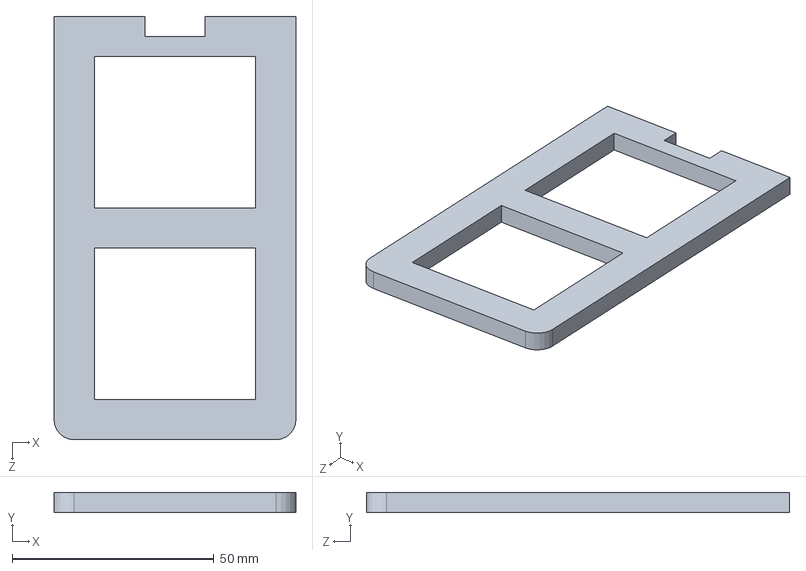
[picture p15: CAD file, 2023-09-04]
CAD models/beam2.SLDPRT
60.0 x 5.00 x 105.0 mm

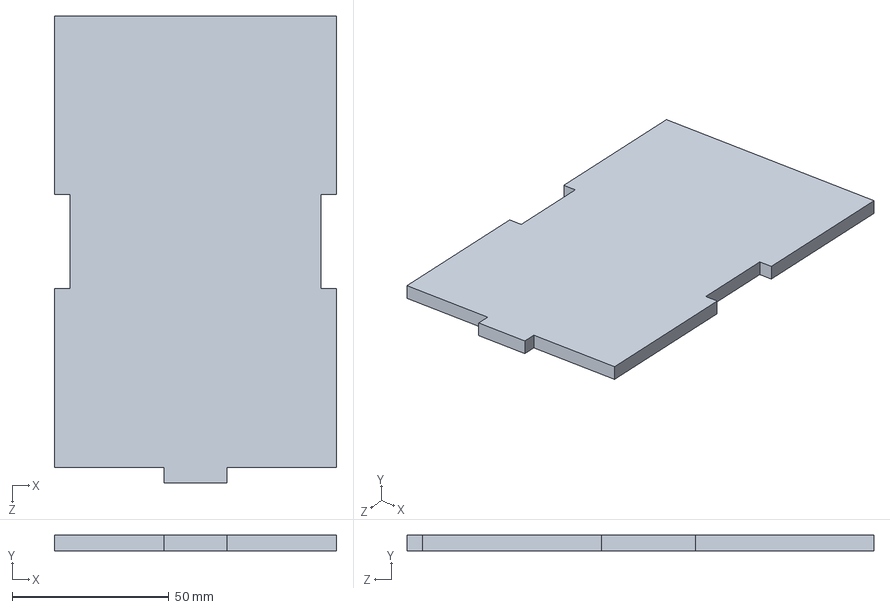
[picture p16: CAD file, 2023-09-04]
CAD models/Battery_rear.SLDPRT
90.0 x 5.00 x 149.0 mm

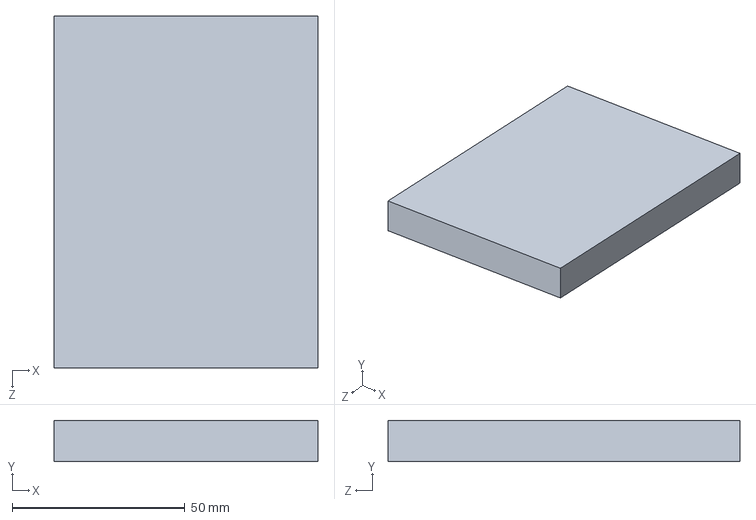
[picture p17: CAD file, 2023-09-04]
CAD models/10_petrifilms.SLDPRT
76.5 x 12.0 x 102.0 mm

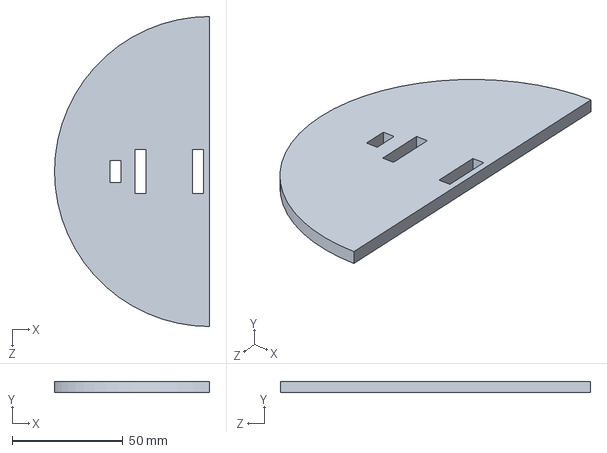
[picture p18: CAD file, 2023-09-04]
CAD models/upper baseup_final.SLDPRT
70.0 x 5.00 x 140.0 mm

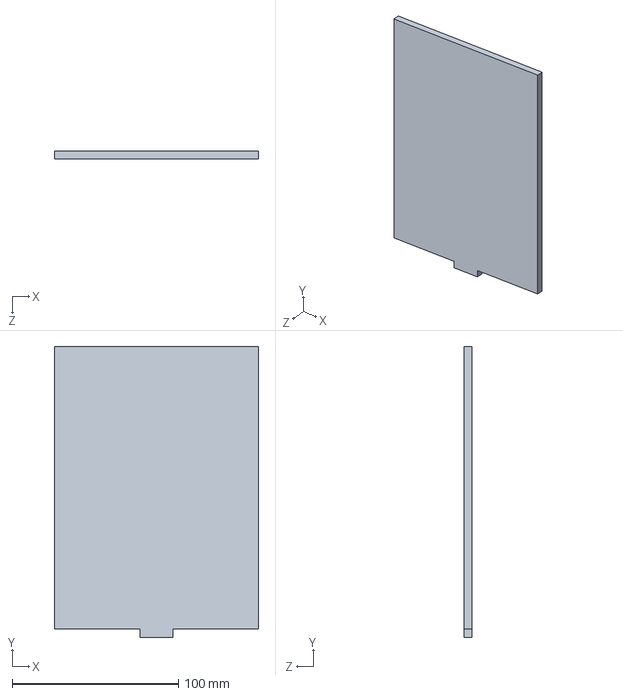
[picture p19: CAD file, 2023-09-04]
CAD models/foam case.SLDPRT
122.8 x 175.0 x 5.00 mm

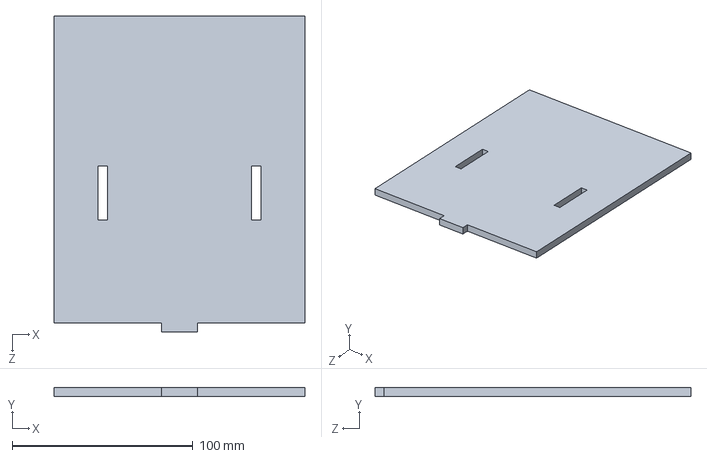
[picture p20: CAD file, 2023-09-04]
CAD models/Battery_front.SLDPRT
139.0 x 5.00 x 175.0 mm

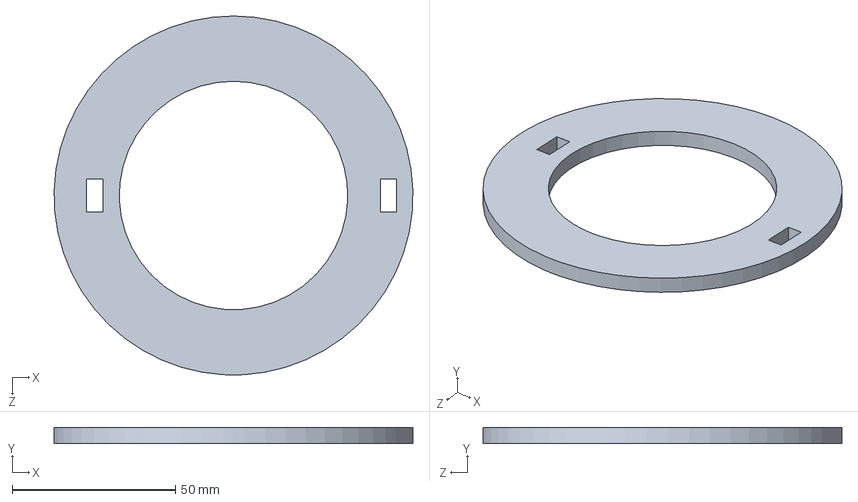
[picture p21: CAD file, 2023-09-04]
CAD models/base_final.SLDPRT
110.0 x 5.00 x 110.0 mm

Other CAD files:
CAD models/alignment.SLDPRT
CAD models/battery_side.SLDPRT
CAD models/upper base_final.SLDPRT
CAD models/drawing.SLDDRW

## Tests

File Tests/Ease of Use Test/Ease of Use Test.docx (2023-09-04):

Conducting an Incubation

Context:

Our Goal:

Assess ease of use of our prototype

Product Information:

Our team has created an incubator for remote water sanitation testing in low resources settings. The incubator is separated into two chambers, the electronics and incubation chamber. We will use Petrifilms and incubate them for 24 - 48 hours to assess water quality. A live digital display of the temperature readings can be seen protruding from the cap of the thermos.

Your Goal:

Start an incubation test

Instructions:

Step 1: Take Petrifilms (stack of 10 max) and place them in the shelf in vertical orientation. The side that “opens” should be pointing upwards out of the shelf.

Step 2: Take the shelf and place it in the “incubation chamber”

Step 3: Adjust location of the temperature sensor so that it is either above or in the “incubation chamber”

Step 4: Take the female wire connector* for the digital display and thread it through the cap of the thermos. Once the wire is through the cap, connect the digital display to the female wire connector.

*Note:

The female wire connector mentioned above is 4 individual female wire connectors that are taped together. The 4 individual wires are black, red, blue, and yellow.

Warning:

Digital display must be connected to the system before turning the system on, or the digital display will NOT turn on. If you turn the system on after connecting the display and the display still doesn’t turn on, unplug the digital display and flip the connections, and try again.

Step 5: Flick the switch on the battery to turn on the system and begin incubation (o → -). Green lights should illuminate from the battery, implying that it is on.

Step 6: Screw on the lid of the thermos. Live temperature readings can be seen on the digital display that protrudes out the top. Please allow 24 - 48 hours for a successful incubation.

Additional Assistance (Optional):

Please refer to these images if you are having difficulty using the device.

- Outside View of Final Solution (https://drive.google.com/file/d/13Jc5LOd9OdwGqFzZs9gYkMpQh3Qa8kuO/view?usp=sharing)
- Shelf (https://drive.google.com/file/d/1VPvUYnY_WPY_CkTKkHqnCs5iyFgZ3ZQT/view?usp=sharing)
- Incubation Chamber (https://drive.google.com/file/d/1Vl0eNMv4kqXfAasvQTcg8jxqjhOQQBGS/view?usp=sharing)

Please refer to this video demonstration (https://youtu.be/XZvEMkBjWKY) if you are having difficulty using the device.

Ranking | Scale of Ease of Use
5 | Simple to use with just instructions, no additional pictures or videos necessary
4 | Somewhat simple to use with just instructions, pictures were necessary to use correctly
3 | Confusing to use with just instructions, pictures and videos were necessary to use correctly
2 | Difficult to use, requires hands on assistance or instruction from another party
1 | Nearly impossible to use, requires an expert to use

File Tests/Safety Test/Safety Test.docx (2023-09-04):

Safety Test

Summary:

- Dr. Gary Woods said everything looks good and should be safe

Recommendations (bold = feasible to adjust before final evaluation):

- Trim wires connected to button drive
  - Little bit of copper exposed
- Move temp sensor to be directly where petrifilms are
  - This way we know if Petrifilms are at ideal temperature
- Wrap up uncovered portions with electrical tape
  - Don’t want these portions cutting other wires
- Test max heat without control system
  - So we know max temperature that our system could reach; need to know if this is a safety concern
- Detach heating pad from wall
  - Significant amount of energy consumed from heating up inner wall of thermos
- Thicker wires for heating system
  - Would be ideal cuz this part requires more current
- Add something around battery to prevent it from sustaining water damage
  - If Petrifilms should leak for whatever reason, we want to have something already protecting the battery
- Power relay thing to turn of system incase something goes wrong
  - This would be a neat and important safety feature
- Use PCB or connector for Arduino Mega
  - Just some way to streamline and clean up wires

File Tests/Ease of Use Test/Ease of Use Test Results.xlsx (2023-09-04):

Run # | Rating: | Feedback:
1 | 4
2 | 4 | Maybe just have photos readily available (this will be determined after this test)
3 | 5
4 | 3 | Add picture of "female connector" part
5 | 4
6 | 3
7 | 4 | Add picture of Petrifilms
8 | 3 | Add more pictures, but new video makes it very clear!
9 | 4
10 | 4
11 | 5 | Hardest part was getting through the wires
 | 3.909090909

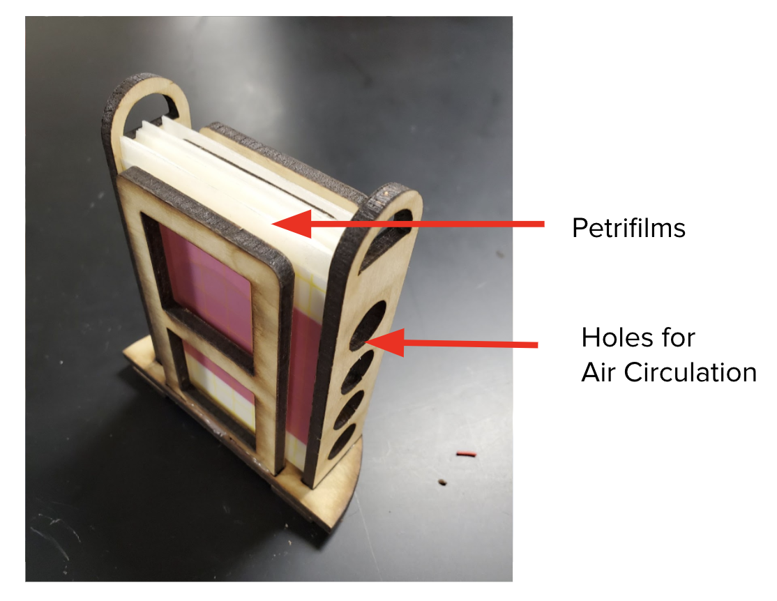
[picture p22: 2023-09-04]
Tests/Ease of Use Test/Shelf.png

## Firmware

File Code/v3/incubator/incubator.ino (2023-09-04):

/*
 * SSD1306 code from: https://randomnerdtutorials.com/guide-for-oled-display-with-arduino/
 */
#include <Wire.h>
#include <Adafruit_GFX.h>     
#include <Adafruit_SSD1306.h>
// #include <DallasTemperature.h>// DS18B20 lib
#include <MsTimer2.h>         
#include <SPI.h>
#include <SD.h>

#define SCREEN_WIDTH 128
#define SCREEN_HEIGHT 32
#define OLED_RESET 4
#define TEMP0 A3
#define ONE_WIRE_BUS 2 
#define WARMER 5
#define tim 1000 // timer, set as 1k ms
#define BUZZER 13 // pin D13
// OLED parameter
Adafruit_SSD1306 display(SCREEN_WIDTH, SCREEN_HEIGHT, &Wire, OLED_RESET);

File myFile;
//OneWire oneWire(ONE_WIRE_BUS);
//DallasTemperature sensors(&oneWire);

_Bool timer_state;        //timer status
unsigned char temps[80];  //store temp value
unsigned char val ;       //time of storing temperature
unsigned int beep_time;   //unacceptable time 
unsigned int beep_begin = 180;//start beeping time
unsigned int beep_end = 180;  //total beeping time(s)
float temp;
float sum = 0.0;
bool initialized;

void setup() {
  Serial.begin(9600);
  Wire.begin();     

  
//  sensors.begin();  // initialize DS18B20 lib

  pinMode(10, OUTPUT);
  if (!SD.begin()) {
    Serial.println("initialization failed!");
  }
  
  
  if(!display.begin(SSD1306_SWITCHCAPVCC, 0x3C)) { 
    Serial.println(F("SSD1306 allocation failed"));
    for(;;); // Don't proceed, loop forever
  }
  
  
  MsTimer2::set(tim, refresh);
  MsTimer2::start();

  // Initialize pins
  pinMode(TEMP0, INPUT);
  
  pinMode(BUZZER, OUTPUT);
  digitalWrite(BUZZER, LOW);
  pinMode(WARMER, OUTPUT);
  digitalWrite(WARMER, LOW);
  
  display.clearDisplay();
  unsigned char i;
  // At beginning, OLED screen will just show a flat line for 30
  for (i = 0; i < 80; i++) {       
    temps[i] = 30;
  }

  initialized = false;

}

void loop() {
  if (timer_state == true) {
    /*
    sensors.requestTemperatures();            // request temp
    float temp = sensors.getTempCByIndex(0);
    */
    // read temperature and update OLED screen
    temp = read_temp();
    Serial.print(temp);
    Serial.println(" C"); // serialport send temp data
    Temp_coord(temp);     // change temp into coordinates
    Temp_display(temp);   // OLED show temp
    Warm(temp);           // heater and BUZZER control
    temp_save(temp);      // store temp data
    timer_state = false;
  }
}

void refresh() {   
  timer_state = true;
}

void Temp_display(float temp) { //OLED display temp，input=temp
  display.clearDisplay();       // clear screen
  display.setTextColor(WHITE);  // set while to be visable
  display.setTextSize(1);       //set text size
  display.setCursor(85, 0);     //set cursor place
  display.print("Temp:");       //words
  display.setCursor(85, 15);    //set cursor place
  display.print((String)temp);          //show temp
  display.print("C");
  display.drawLine(0, 0, 0, 30, WHITE);   //draw Y axis
  display.drawLine(0, 30, 80, 30, WHITE); //draw X axis

  Display_temps();              //show temp point
  display.display();            //update screen
}

void Warm(float temp) {          //decide to warm&alarm or not
  if (temp <= 34.5) {               //below 34.5 celcius
    digitalWrite(WARMER, HIGH);  //start heater
  }
  if (temp >= 35.5) {         //above 35.5
    digitalWrite(WARMER, LOW);   //heater off
  }
  if (temp <= 34 || temp > 36) {
    beep_time += (tim / 1000);
  }
  else {
    initialized = true;
    beep_time = 0;
  }
  if (beep_time > beep_begin && beep_time < beep_begin + beep_end && initialized) { 
    //unacceptable temp for 3 min，3X60=180s
    digitalWrite(BUZZER, HIGH);
  }
  else {
    digitalWrite(BUZZER, LOW);
  }
  if (beep_time  >= beep_begin + beep_end) {
    beep_time = 0;
  }
}

void Display_temps() {
  unsigned char i;
  for (i = 0; i <= 79; i++) {    //show temp points chronologically
    display.drawPixel(i, temps[i], WHITE);
  }
  display.display();
}

float read_temp() {
  // Take average of a couple reads
  unsigned char i;
  sum = 0;
  for (i = 0; i < 5; i++) {
    sum += ((analogRead(TEMP0) * 500.0) / 1024.0);
  }
  sum /= 5.0;
  return sum;
  
  //return ((analogRead(TEMP0) * 500.0) / 1024.0); // reading * 5000 / 1024 calibrates ADC to volts, and division by 10 calibrates to celcius
}

void Temp_coord(float temp) {
  unsigned char i;
  if (val < 79) {   //first 79 points show as it is
    temps[val] = 60 - char(temp * 1.5 + 0.5);
    val++;
  }
  else {
    for (i = 0; i <= 79; i++) {  //80 and more, push the first point
      temps[i] = temps[i + 1];
    }
    temps[79] = 60 - char(temp * 1.5  + 0.5); //fill in the last temp as the 79th point
  }
}

void temp_save(float temp) {
  //open file, only one at a time
  myFile = SD.open("temp.CSV", FILE_WRITE);
  // if open, write down
  if (myFile)
  {
    Serial.print("Writing to test.txt...");
    time_disposal();
    myFile.print(temp);
    myFile.println();
    // myFile.println("C");
    // close file
    myFile.close();
    Serial.println("done.");
  }
  else
  {
    //if not open, show this
    Serial.println("error opening test.txt");
  }
}

void time_disposal() {  //read and show as hour, min, and second
  myFile.print(millis() / 1000);
  myFile.print(",");      //write in chronological order
}
